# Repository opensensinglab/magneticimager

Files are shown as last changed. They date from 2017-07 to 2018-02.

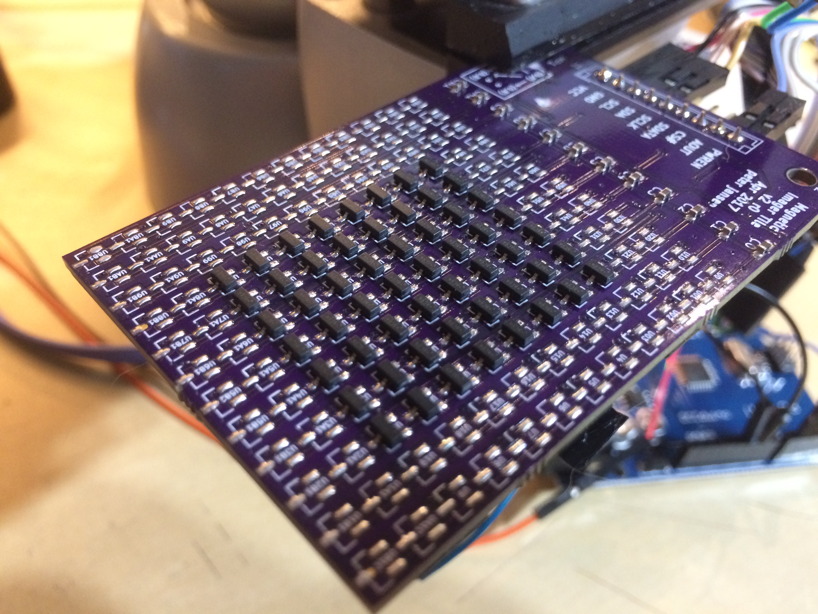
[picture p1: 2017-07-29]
hardware/version2r0/magnetic_tile_top.JPG

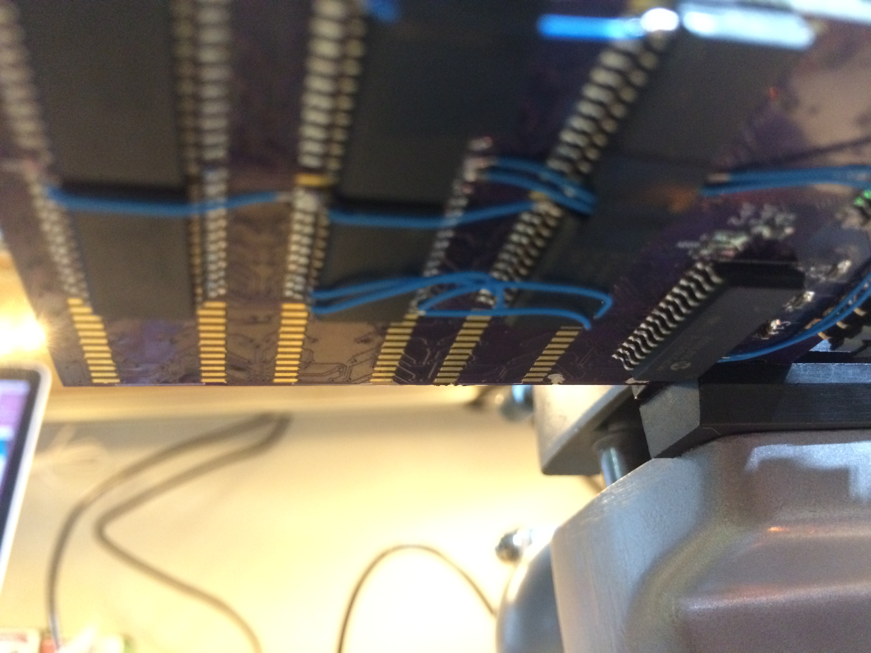
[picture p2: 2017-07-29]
hardware/version2r0/magnetic_tile_bottom.JPG

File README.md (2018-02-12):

Magnetic Imaging Tile
======

Work-in-progress.  Please use at your own risk. <br>

This is a board intended to function as a "magnetic field camera", and visualize magnetic fields. 

### Version 3.0

The major advancement of v3.0 is a dramatic increase in the speed with which the tile data can be read out.  I have achieved ~2000 frames per second (fps), which allows visualizing even quickly varying fields (e.g. those in a 60Hz transformer, or a moving motor), but it's likely that the tile can achieve even higher framerates.  Version 3.0 reduces the size of the tile to an 8x8 grid of hall effect sensors (64 total), arrayed in a 4mm grid.  The boards should also still be tile-able, with up to 4 of the boards tileable with minimal borders to create a 16x16 array. 

For more information (and a video of the v3.0 tile in use), please see: 
https://hackaday.io/project/18518-iteration-8/log/91551-a-third-high-speed-magnetic-imager-tile-draft

### Version 2.0

Version 2.0 consists of an array of 12x12 hall effect sensors (144 total) that sense magnetic fields, arrayed in a 4mm grid.  Each sensor is connected to an array of analog switches, that allow an individual sensor to be addressed.  Read out is accomplished one magnetic "pixel" at a time, selecting a given hall sensor from the array, reading it's value (either using the internal ADC, or an external ADC), and repeating this process until the entire array has been read out.  

The current array is designed to be tile-able, with up to four of the boards (24x24 magnetic field sensors) arrayed together. 

The Arduino firmware has a framerate of approximately 10 frames per second, when the image data is streamed over the serial port and displayed using the Processing visualization.  The Raspberry Pi Python example achieves approximately 30fps.  The array itself is likely capable of much higher speeds, but one of the major limiting factors is currently the speed of the I2C I/O multiplexer (used to select which magnetometer to read from). 

For more information (and a video of the v2.0 tile in use), please see: 
https://hackaday.io/project/18518-iteration-8/log/64376-a-magnetic-imager-tile

# Open Source

This project is open source software and hardware, and is released under various open licenses.

# Disclaimer

**DISCLAIMER OF WARRANTIES AND LIMITATION OF LIABILITY.**

UNLESS OTHERWISE SEPARATELY UNDERTAKEN BY THE LICENSOR, TO THE EXTENT POSSIBLE, THE LICENSOR OFFERS THE LICENSED MATERIAL AS-IS AND AS-AVAILABLE, AND MAKES NO REPRESENTATIONS OR WARRANTIES OF ANY KIND CONCERNING THE LICENSED MATERIAL, WHETHER EXPRESS, IMPLIED, STATUTORY, OR OTHER. THIS INCLUDES, WITHOUT LIMITATION, WARRANTIES OF TITLE, MERCHANTABILITY, FITNESS FOR A PARTICULAR PURPOSE, NON-INFRINGEMENT, ABSENCE OF LATENT OR OTHER DEFECTS, ACCURACY, OR THE PRESENCE OR ABSENCE OF ERRORS, WHETHER OR NOT KNOWN OR DISCOVERABLE. WHERE DISCLAIMERS OF WARRANTIES ARE NOT ALLOWED IN FULL OR IN PART, THIS DISCLAIMER MAY NOT APPLY TO YOU.

TO THE EXTENT POSSIBLE, IN NO EVENT WILL THE LICENSOR BE LIABLE TO YOU ON ANY LEGAL THEORY (INCLUDING, WITHOUT LIMITATION, NEGLIGENCE) OR OTHERWISE FOR ANY DIRECT, SPECIAL, INDIRECT, INCIDENTAL, CONSEQUENTIAL, PUNITIVE, EXEMPLARY, OR OTHER LOSSES, COSTS, EXPENSES, OR DAMAGES ARISING OUT OF THIS PUBLIC LICENSE OR USE OF THE LICENSED MATERIAL, EVEN IF THE LICENSOR HAS BEEN ADVISED OF THE POSSIBILITY OF SUCH LOSSES, COSTS, EXPENSES, OR DAMAGES. WHERE A LIMITATION OF LIABILITY IS NOT ALLOWED IN FULL OR IN PART, THIS LIMITATION MAY NOT APPLY TO YOU.

THE DISCLAIMER OF WARRANTIES AND LIMITATION OF LIABILITY PROVIDED ABOVE SHALL BE INTERPRETED IN A MANNER THAT, TO THE EXTENT POSSIBLE, MOST CLOSELY APPROXIMATES AN ABSOLUTE DISCLAIMER AND WAIVER OF ALL LIABILITY.

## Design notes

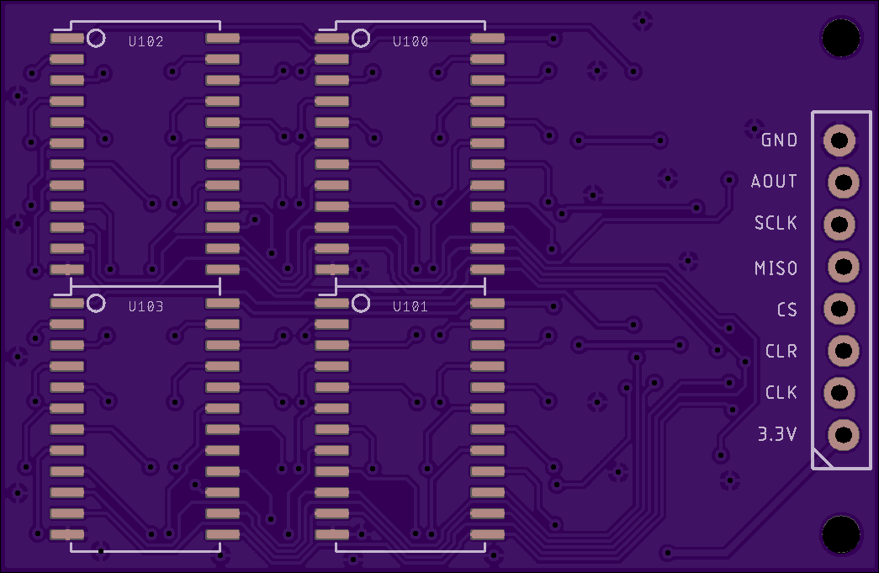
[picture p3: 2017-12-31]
hardware/version3r0/board_bottom.png

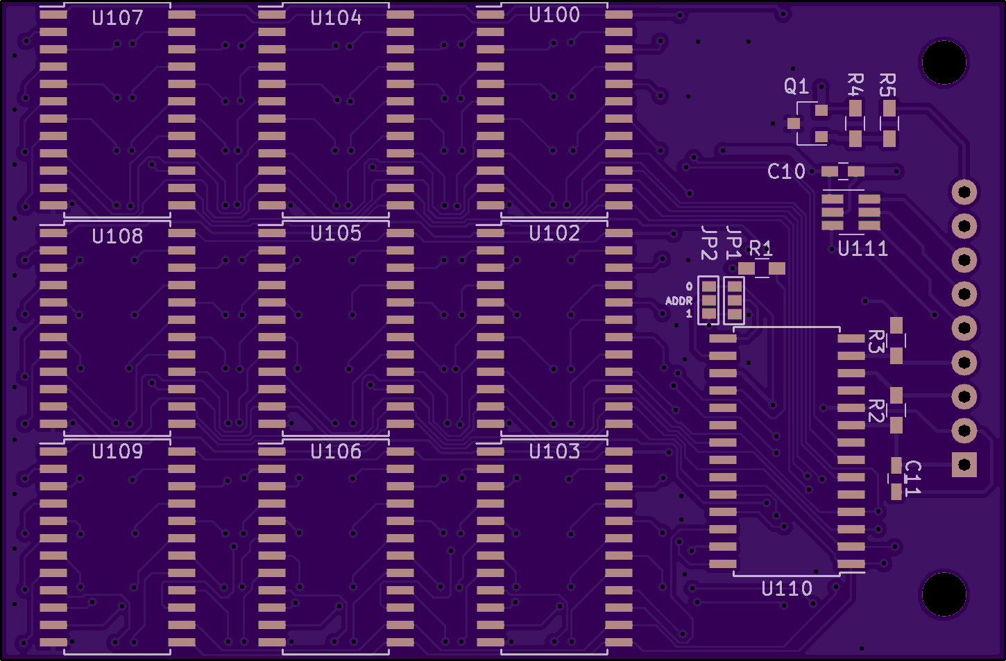
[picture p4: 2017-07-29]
hardware/version2r0/board_bottom.png

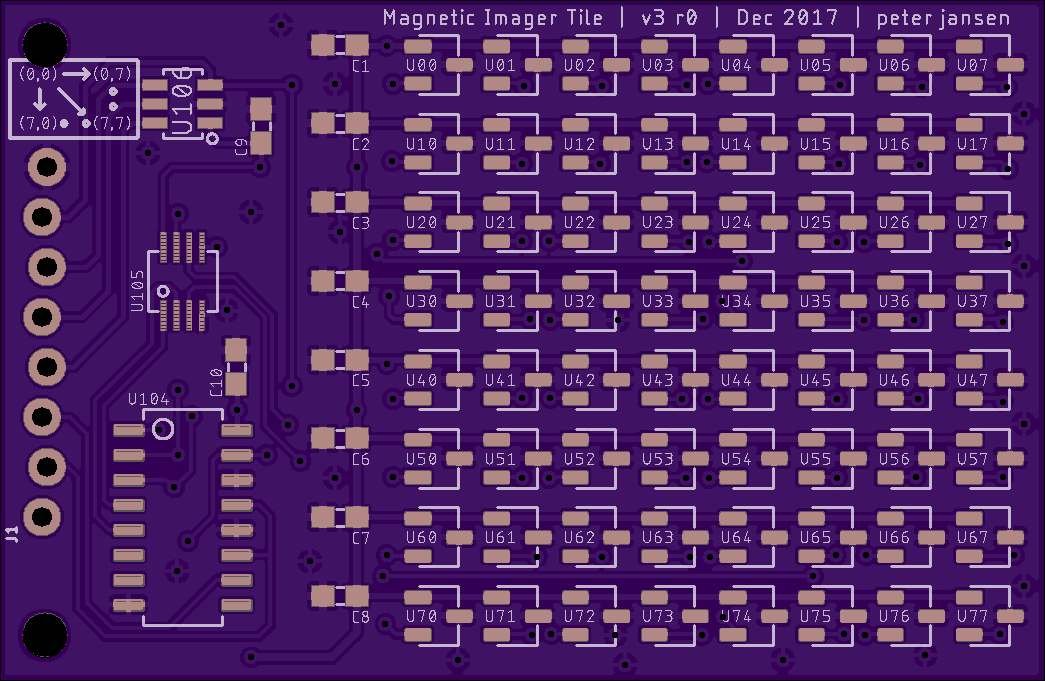
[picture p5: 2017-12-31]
hardware/version3r0/board_top.png

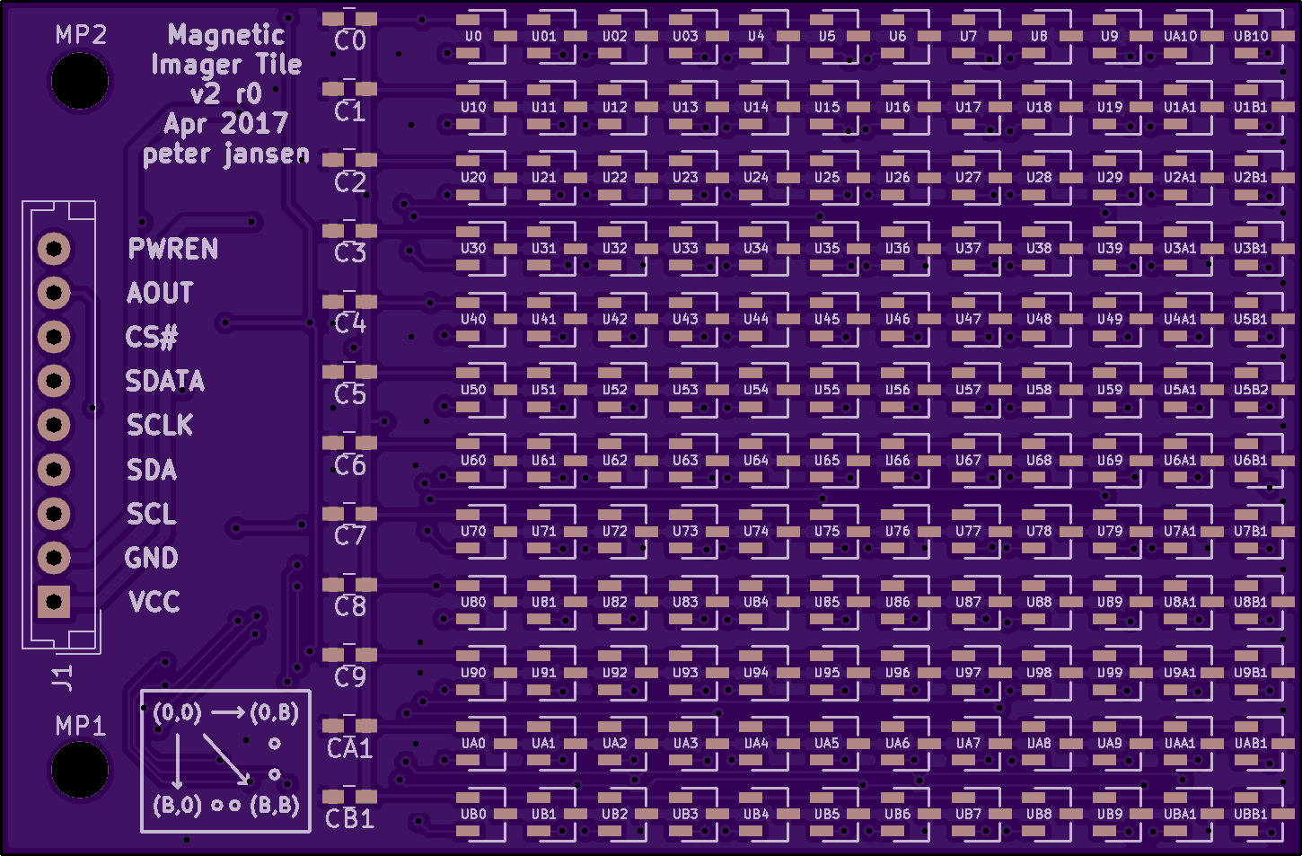
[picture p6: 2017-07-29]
hardware/version2r0/board_top.png

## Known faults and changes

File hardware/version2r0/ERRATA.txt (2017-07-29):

KNOWN ERRATA:
Version 2 revision 0
- The MOSFET to enable power (Q1) did not function, and is likely wired incorrectly.  The fix for this (if you've already made one of the boards without fixing the source) is to remove Q1, and add a small jumper so that the power is always enabled.

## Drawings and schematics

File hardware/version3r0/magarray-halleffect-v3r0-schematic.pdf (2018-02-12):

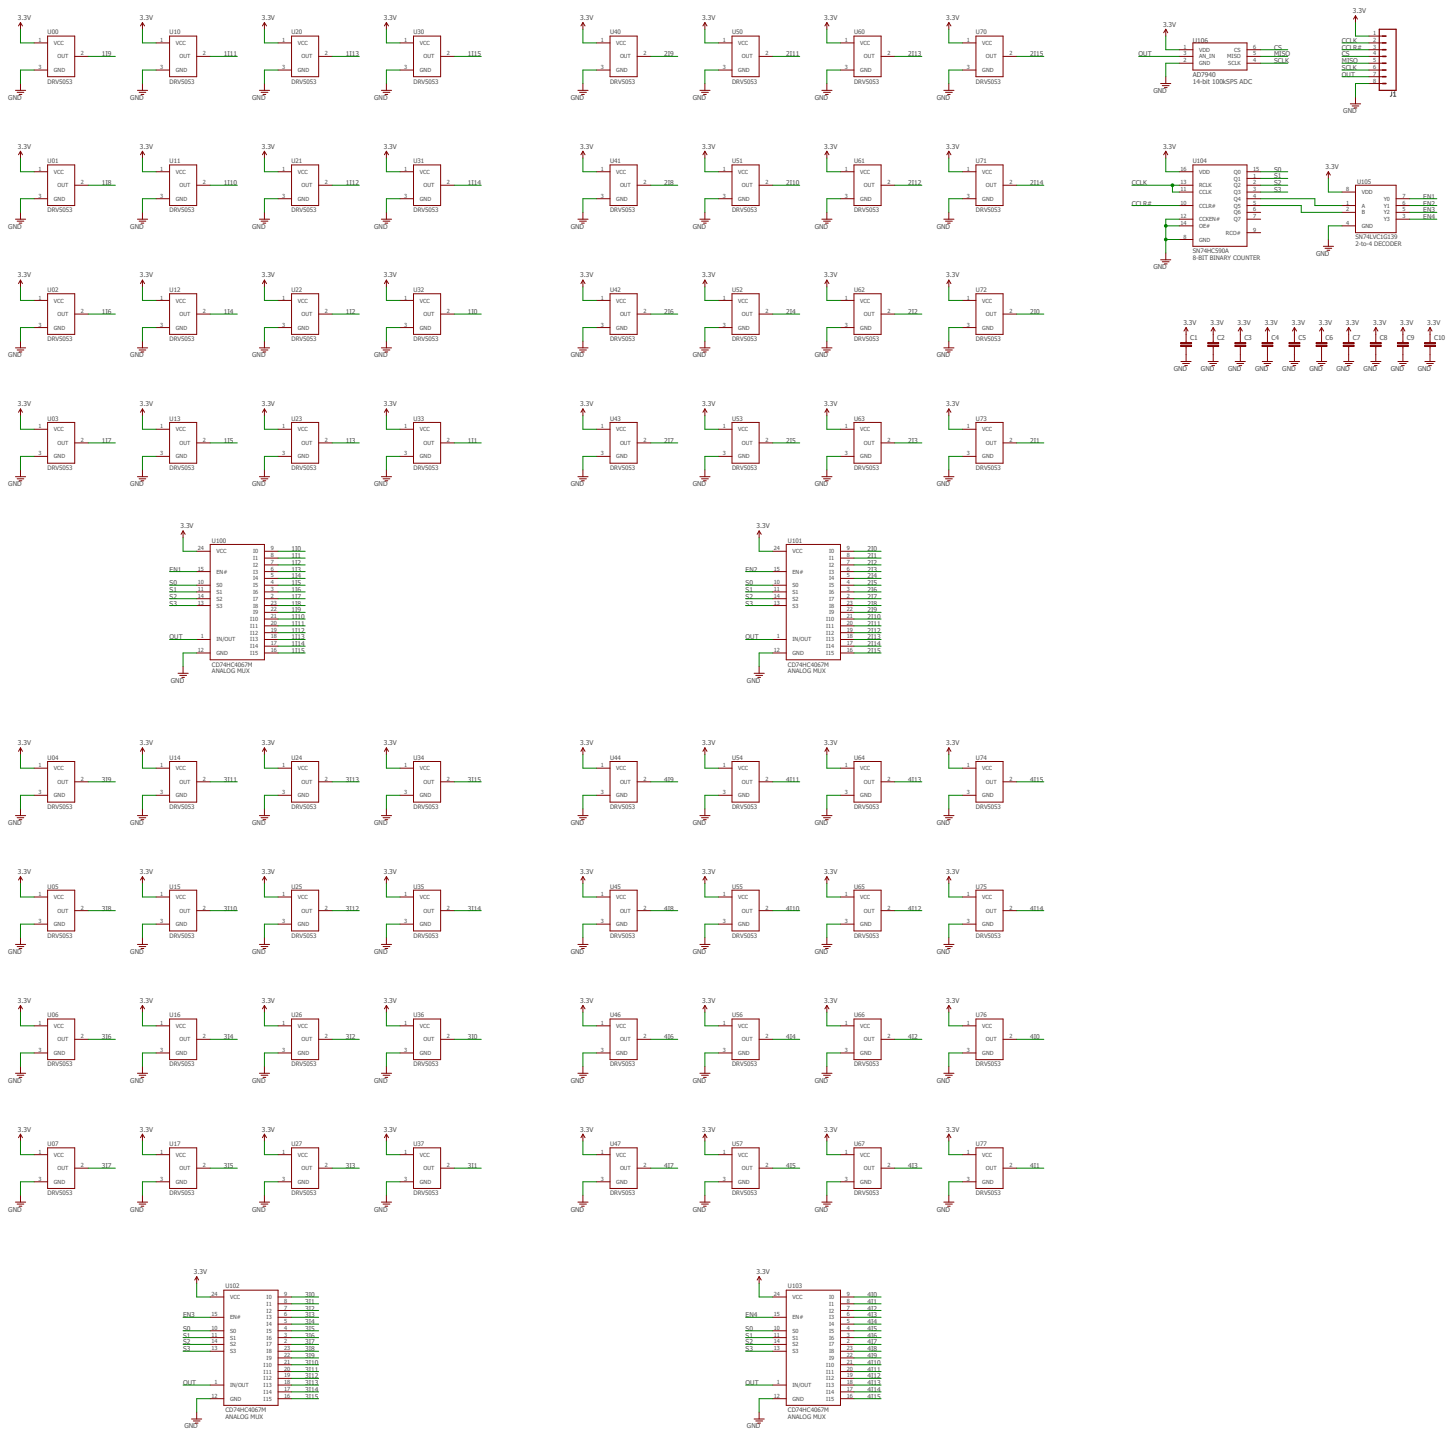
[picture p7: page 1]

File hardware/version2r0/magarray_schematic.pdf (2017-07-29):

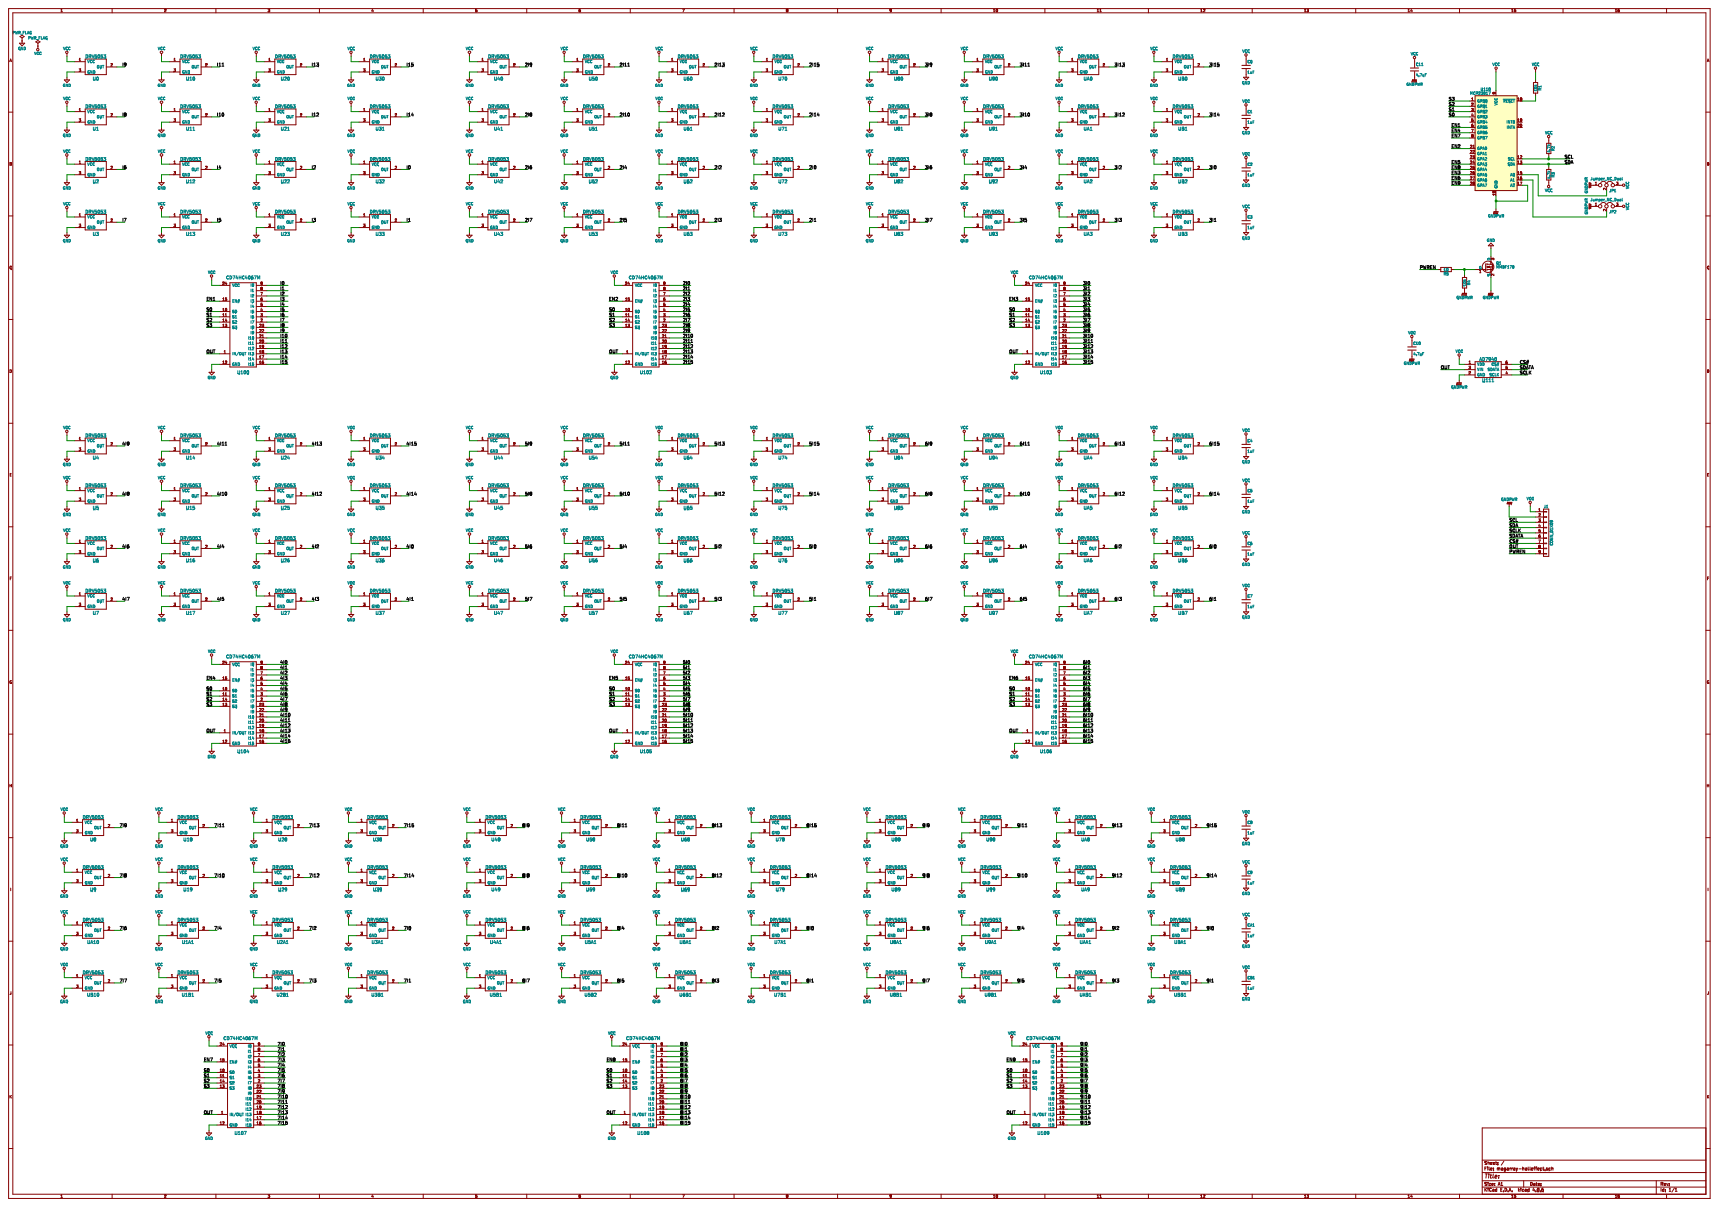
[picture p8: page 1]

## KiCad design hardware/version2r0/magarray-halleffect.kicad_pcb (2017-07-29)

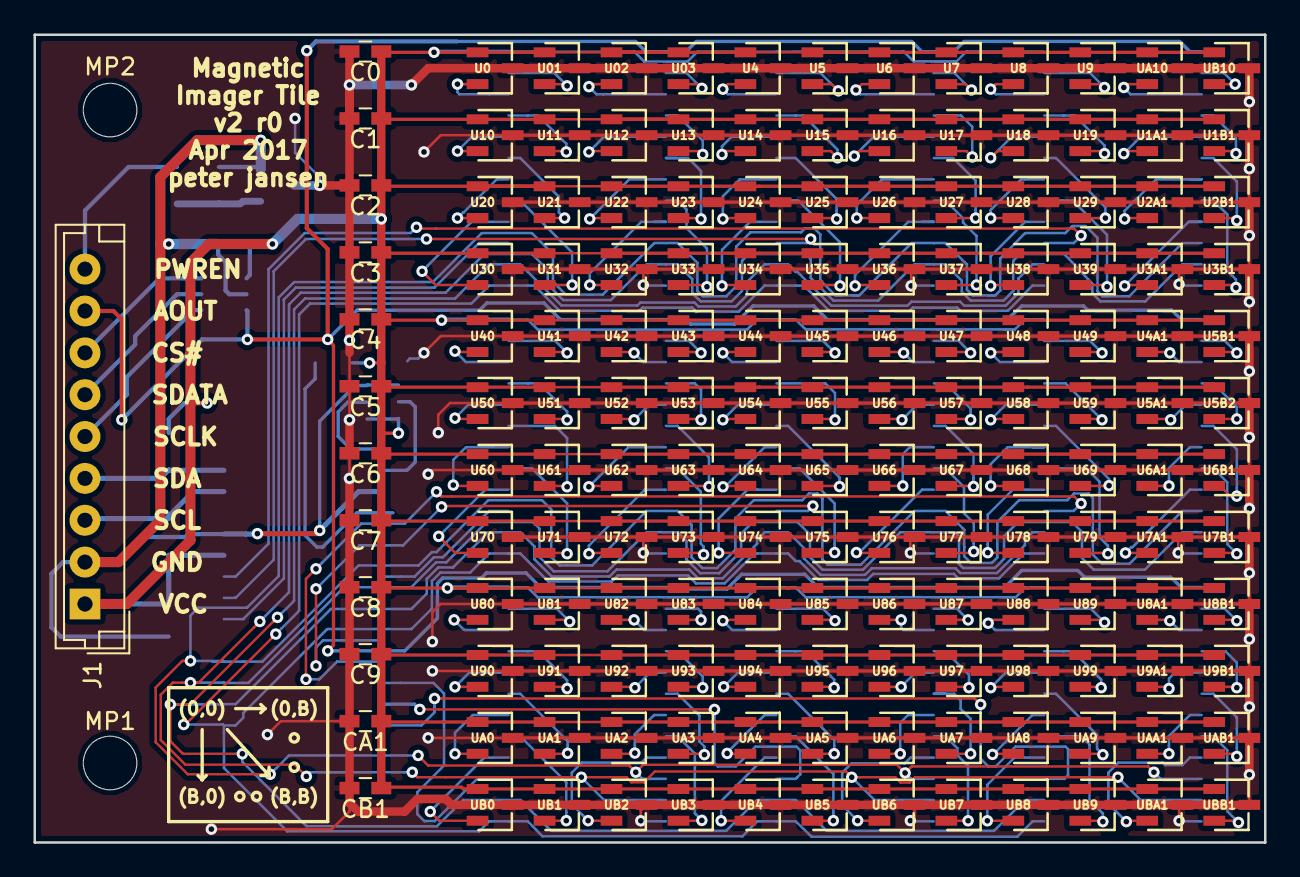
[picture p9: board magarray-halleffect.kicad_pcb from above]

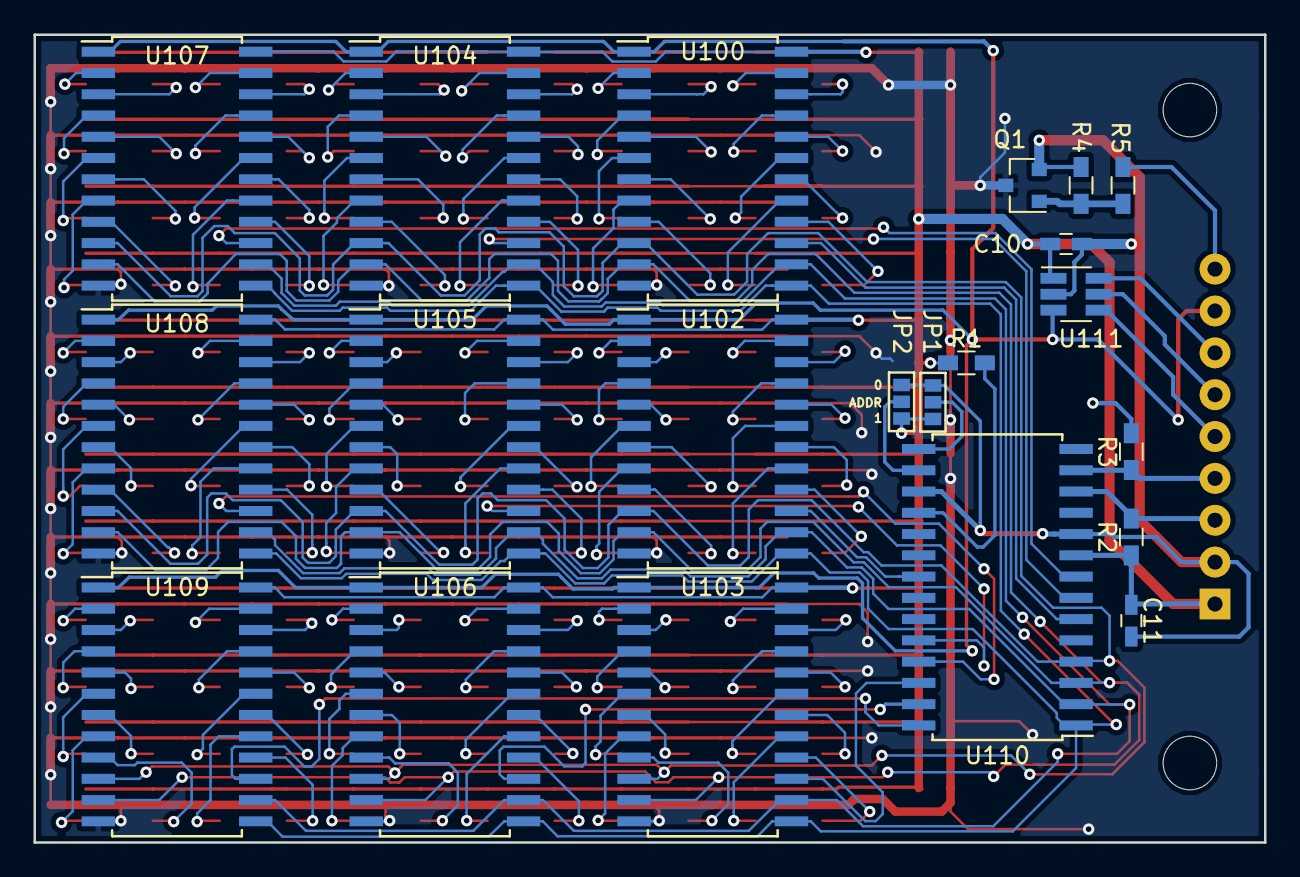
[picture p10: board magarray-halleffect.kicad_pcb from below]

Board: 2 copper layers, 73.5 x 48.2 mm, 180 parts (21 on the bottom side), 171 nets.

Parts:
C0, C1, C2, C3, C4, C5, C6, C7, C8, C9: 1uF; C_0603_HandSoldering
C10, C11: 4.7uF; C_0603_HandSoldering
CA1: 1uF; C_0603_HandSoldering
CB1: 1uF; C_0603_HandSoldering
J1: CONN_01X09; JST_EH_B09B-EH-A_09x2.50mm_Straight
JP1, JP2: Jumper_NC_Dual; SOLDERJUMPER-2WAY
MP1, MP2: MountingHole_3.2mm_M3
Q1: MMBF170; SOT-23
R1, R4: 10k; R_0603_HandSoldering
R2, R3: 4.7k; R_0603_HandSoldering
R5: 10; R_0603_HandSoldering
U0, U01, U1A1, U1B1, U02, U2A1, U2B1, U03, U3A1, U3B1, U4, U4A1, U5, U5A1, U5B1, U5B2, U6, U6A1, U6B1, U7, U7A1, U7B1, U8, U8A1, U8B1, U9, U9A1, U9B1, U10, U11, U12, U13, U14, U15, U16, U17, U18, U19, U20, U21, U22, U23, U24, U25, U26, U27, U28, U29, U30, U31, U32, U33, U34, U35, U36, U37, U38, U39, U40, U41, U42, U43, U44, U45, U46, U47, U48, U49, U50, U51, U52, U53, U54, U55, U56, U57, U58, U59, U60, U61, U62, U63, U64, U65, U66, U67, U68, U69, U70, U71, U72, U73, U74, U75, U76, U77, U78, U79, U80, U81, U82, U83, U84, U85, U86, U87, U88, U89, U90, U91, U92, U93, U94, U95, U96, U97, U98, U99: DRV5053; SOT-23
U100, U102, U103, U104, U105, U106, U107, U108, U109: CD74HC4067M; SOIC-24W_7.5x15.4mm_Pitch1.27mm
U110: MCP23017; SOIC-28W_7.5x17.9mm_Pitch1.27mm
U111: AD7940; SOT-23-6_Handsoldering
UA0, UA1, UA2, UA3, UA4, UA5, UA6, UA7, UA8, UA9, UA10: DRV5053; SOT-23
UAA1: DRV5053; SOT-23
UAB1: DRV5053; SOT-23
UB0, UB1, UB2, UB3, UB4, UB5, UB6, UB7, UB8, UB9, UB10: DRV5053; SOT-23
UBA1: DRV5053; SOT-23
UBB1: DRV5053; SOT-23

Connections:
/2I0: U72.2, U102.9
/2I1: U73.2, U102.8
/2I2: U62.2, U102.7
/2I3: U63.2, U102.6
/2I4: U52.2, U102.5
/2I5: U53.2, U102.4
/2I6: U42.2, U102.3
/2I7: U43.2, U102.2
/2I8: U41.2, U102.23
/2I9: U40.2, U102.22
/2I10: U51.2, U102.21
/2I11: U50.2, U102.20
/2I12: U61.2, U102.19
/2I13: U60.2, U102.18
/2I14: U71.2, U102.17
/2I15: U70.2, U102.16
/3I0: U103.9, UB2.2
/3I1: U103.8, UB3.2
/3I2: U103.7, UA2.2
/3I3: U103.6, UA3.2
/3I4: U92.2, U103.5
/3I5: U93.2, U103.4
/3I6: U82.2, U103.3
/3I7: U83.2, U103.2
/3I8: U81.2, U103.23
/3I9: U80.2, U103.22
/3I10: U91.2, U103.21
/3I11: U90.2, U103.20
/3I12: U103.19, UA1.2
/3I13: U103.18, UA0.2
/3I14: U103.17, UB1.2
/3I15: U103.16, UB0.2
/4I0: U36.2, U104.9
/4I1: U37.2, U104.8
/4I2: U26.2, U104.7
/4I3: U27.2, U104.6
/4I4: U16.2, U104.5
/4I5: U17.2, U104.4
/4I6: U6.2, U104.3
/4I7: U7.2, U104.2
/4I8: U5.2, U104.23
/4I9: U4.2, U104.22
/4I10: U15.2, U104.21
/4I11: U14.2, U104.20
/4I12: U25.2, U104.19
/4I13: U24.2, U104.18
/4I14: U35.2, U104.17
/4I15: U34.2, U104.16
/5I0: U76.2, U105.9
/5I1: U77.2, U105.8
/5I2: U66.2, U105.7
/5I3: U67.2, U105.6
/5I4: U56.2, U105.5
/5I5: U57.2, U105.4
/5I6: U46.2, U105.3
/5I7: U47.2, U105.2
/5I8: U45.2, U105.23
/5I9: U44.2, U105.22
/5I10: U55.2, U105.21
/5I11: U54.2, U105.20
/5I12: U65.2, U105.19
/5I13: U64.2, U105.18
/5I14: U75.2, U105.17
/5I15: U74.2, U105.16
/6I0: U106.9, UB6.2
/6I1: U106.8, UB7.2
/6I2: U106.7, UA6.2
/6I3: U106.6, UA7.2
/6I4: U96.2, U106.5
/6I5: U97.2, U106.4
/6I6: U86.2, U106.3
/6I7: U87.2, U106.2
/6I8: U85.2, U106.23
/6I9: U84.2, U106.22
/6I10: U95.2, U106.21
/6I11: U94.2, U106.20
/6I12: U106.19, UA5.2
/6I13: U106.18, UA4.2
/6I14: U106.17, UB5.2
/6I15: U106.16, UB4.2
/7I0: U3A1.2, U107.9
/7I1: U3B1.2, U107.8
/7I2: U2A1.2, U107.7
/7I3: U2B1.2, U107.6
/7I4: U1A1.2, U107.5
/7I5: U1B1.2, U107.4
/7I6: U107.3, UA10.2
/7I7: U107.2, UB10.2
/7I8: U9.2, U107.23
/7I9: U8.2, U107.22
/7I10: U19.2, U107.21
/7I11: U18.2, U107.20
/7I12: U29.2, U107.19
/7I13: U28.2, U107.18
/7I14: U39.2, U107.17
/7I15: U38.2, U107.16
/8I0: U7A1.2, U108.9
/8I1: U7B1.2, U108.8
/8I2: U6A1.2, U108.7
/8I3: U6B1.2, U108.6
/8I4: U5A1.2, U108.5
/8I5: U5B2.2, U108.4
/8I6: U4A1.2, U108.3
/8I7: U5B1.2, U108.2
/8I8: U49.2, U108.23
/8I9: U48.2, U108.22
/8I10: U59.2, U108.21
/8I11: U58.2, U108.20
/8I12: U69.2, U108.19
/8I13: U68.2, U108.18
/8I14: U79.2, U108.17
/8I15: U78.2, U108.16
/9I0: U109.9, UBA1.2
/9I1: U109.8, UBB1.2
/9I2: U109.7, UAA1.2
/9I3: U109.6, UAB1.2
/9I4: U9A1.2, U109.5
/9I5: U9B1.2, U109.4
/9I6: U8A1.2, U109.3
/9I7: U8B1.2, U109.2
/9I8: U89.2, U109.23
/9I9: U88.2, U109.22
/9I10: U99.2, U109.21
/9I11: U98.2, U109.20
/9I12: U109.19, UA9.2
/9I13: U109.18, UA8.2
/9I14: U109.17, UB9.2
/9I15: U109.16, UB8.2
/CS#: J1.7, U111.6
/EN1: U100.15, U110.6
/EN2: U102.15, U110.21
/EN3: U103.15, U110.26
/EN4: U104.15, U110.7
/EN5: U105.15, U110.24
/EN6: U106.15, U110.27
/EN7: U107.15, U110.8
/EN8: U108.15, U110.25
/EN9: U109.15, U110.28
/I0: U32.2, U100.9
/I1: U33.2, U100.8
/I2: U22.2, U100.7
/I3: U23.2, U100.6
/I4: U12.2, U100.5
/I5: U13.2, U100.4
/I6: U02.2, U100.3
/I7: U03.2, U100.2
/I8: U01.2, U100.23
/I9: U0.2, U100.22
/I10: U11.2, U100.21
/I11: U10.2, U100.20
/I12: U21.2, U100.19
/I13: U20.2, U100.18
/I14: U31.2, U100.17
/I15: U30.2, U100.16
/OUT: J1.8, U100.1, U102.1, U103.1, U104.1, U105.1, U106.1, U107.1, U108.1, U109.1, U111.3
/PWREN: J1.9, R5.2
/S0: U100.10, U102.10, U103.10, U104.10, U105.10, U106.10, U107.10, U108.10, U109.10, U110.4
/S1: U100.11, U102.11, U103.11, U104.11, U105.11, U106.11, U107.11, U108.11, U109.11, U110.3
/S2: U100.14, U102.14, U103.14, U104.14, U105.14, U106.14, U107.14, U108.14, U109.14, U110.2
/S3: U100.13, U102.13, U103.13, U104.13, U105.13, U106.13, U107.13, U108.13, U109.13, U110.1
/SCL: J1.3, R2.2, U110.12
/SCLK: J1.5, U111.4
/SDA: J1.4, R3.1, U110.13
/SDATA: J1.6, U111.5
GND: C0.2, C1.2, C2.2, C3.2, C4.2, C5.2, C6.2, C7.2, C8.2, C9.2, CA1.2, CB1.2, Q1.3, U0.3, U01.3, U1A1.3, U1B1.3, U02.3, U2A1.3, U2B1.3, U03.3, U3A1.3, U3B1.3, U4.3, U4A1.3, U5.3, U5A1.3, U5B1.3, U5B2.3, U6.3, U6A1.3, U6B1.3, U7.3, U7A1.3, U7B1.3, U8.3, U8A1.3, U8B1.3, U9.3, U9A1.3, U9B1.3, U10.3, U11.3, U12.3, U13.3, U14.3, U15.3, U16.3, U17.3, U18.3, U19.3, U20.3, U21.3, U22.3, U23.3, U24.3, U25.3, U26.3, U27.3, U28.3, U29.3, U30.3, U31.3, U32.3, U33.3, U34.3, U35.3, U36.3, U37.3, U38.3, U39.3, U40.3, U41.3, U42.3, U43.3, U44.3, U45.3, U46.3, U47.3, U48.3, U49.3, U50.3, U51.3, U52.3, U53.3, U54.3, U55.3, U56.3, U57.3, U58.3, U59.3, U60.3, U61.3, U62.3, U63.3, U64.3, U65.3, U66.3, U67.3, U68.3, U69.3, U70.3, U71.3, U72.3, U73.3, U74.3, U75.3, U76.3, U77.3, U78.3, U79.3, U80.3, U81.3, U82.3, U83.3, U84.3, U85.3, U86.3, U87.3, U88.3, U89.3, U90.3, U91.3, U92.3, U93.3, U94.3, U95.3, U96.3, U97.3, U98.3, U99.3, U100.12, U102.12, U103.12, U104.12, U105.12, U106.12, U107.12, U108.12, U109.12, UA0.3, UA1.3, UA2.3, UA3.3, UA4.3, UA5.3, UA6.3, UA7.3, UA8.3, UA9.3, UA10.3, UAA1.3, UAB1.3, UB0.3, UB1.3, UB2.3, UB3.3, UB4.3, UB5.3, UB6.3, UB7.3, UB8.3, UB9.3, UB10.3, UBA1.3, UBB1.3
GNDPWR: C10.2, C11.2, J1.2, JP1.1, JP2.1, Q1.2, R4.2, U110.10, U110.17, U111.2
unnamed: JP1.2, U110.15
unnamed: JP2.2, U110.16
unnamed: Q1.1, R4.1, R5.1
unnamed: R1.2, U110.18
VCC: C0.1, C1.1, C2.1, C3.1, C4.1, C5.1, C6.1, C7.1, C8.1, C9.1, C10.1, C11.1, CA1.1, CB1.1, J1.1, JP1.3, JP2.3, R1.1, R2.1, R3.2, U0.1, U01.1, U1A1.1, U1B1.1, U02.1, U2A1.1, U2B1.1, U03.1, U3A1.1, U3B1.1, U4.1, U4A1.1, U5.1, U5A1.1, U5B1.1, U5B2.1, U6.1, U6A1.1, U6B1.1, U7.1, U7A1.1, U7B1.1, U8.1, U8A1.1, U8B1.1, U9.1, U9A1.1, U9B1.1, U10.1, U11.1, U12.1, U13.1, U14.1, U15.1, U16.1, U17.1, U18.1, U19.1, U20.1, U21.1, U22.1, U23.1, U24.1, U25.1, U26.1, U27.1, U28.1, U29.1, U30.1, U31.1, U32.1, U33.1, U34.1, U35.1, U36.1, U37.1, U38.1, U39.1, U40.1, U41.1, U42.1, U43.1, U44.1, U45.1, U46.1, U47.1, U48.1, U49.1, U50.1, U51.1, U52.1, U53.1, U54.1, U55.1, U56.1, U57.1, U58.1, U59.1, U60.1, U61.1, U62.1, U63.1, U64.1, U65.1, U66.1, U67.1, U68.1, U69.1, U70.1, U71.1, U72.1, U73.1, U74.1, U75.1, U76.1, U77.1, U78.1, U79.1, U80.1, U81.1, U82.1, U83.1, U84.1, U85.1, U86.1, U87.1, U88.1, U89.1, U90.1, U91.1, U92.1, U93.1, U94.1, U95.1, U96.1, U97.1, U98.1, U99.1, U100.24, U102.24, U103.24, U104.24, U105.24, U106.24, U107.24, U108.24, U109.24, U110.9, U111.1, UA0.1, UA1.1, UA2.1, UA3.1, UA4.1, UA5.1, UA6.1, UA7.1, UA8.1, UA9.1, UA10.1, UAA1.1, UAB1.1, UB0.1, UB1.1, UB2.1, UB3.1, UB4.1, UB5.1, UB6.1, UB7.1, UB8.1, UB9.1, UB10.1, UBA1.1, UBB1.1

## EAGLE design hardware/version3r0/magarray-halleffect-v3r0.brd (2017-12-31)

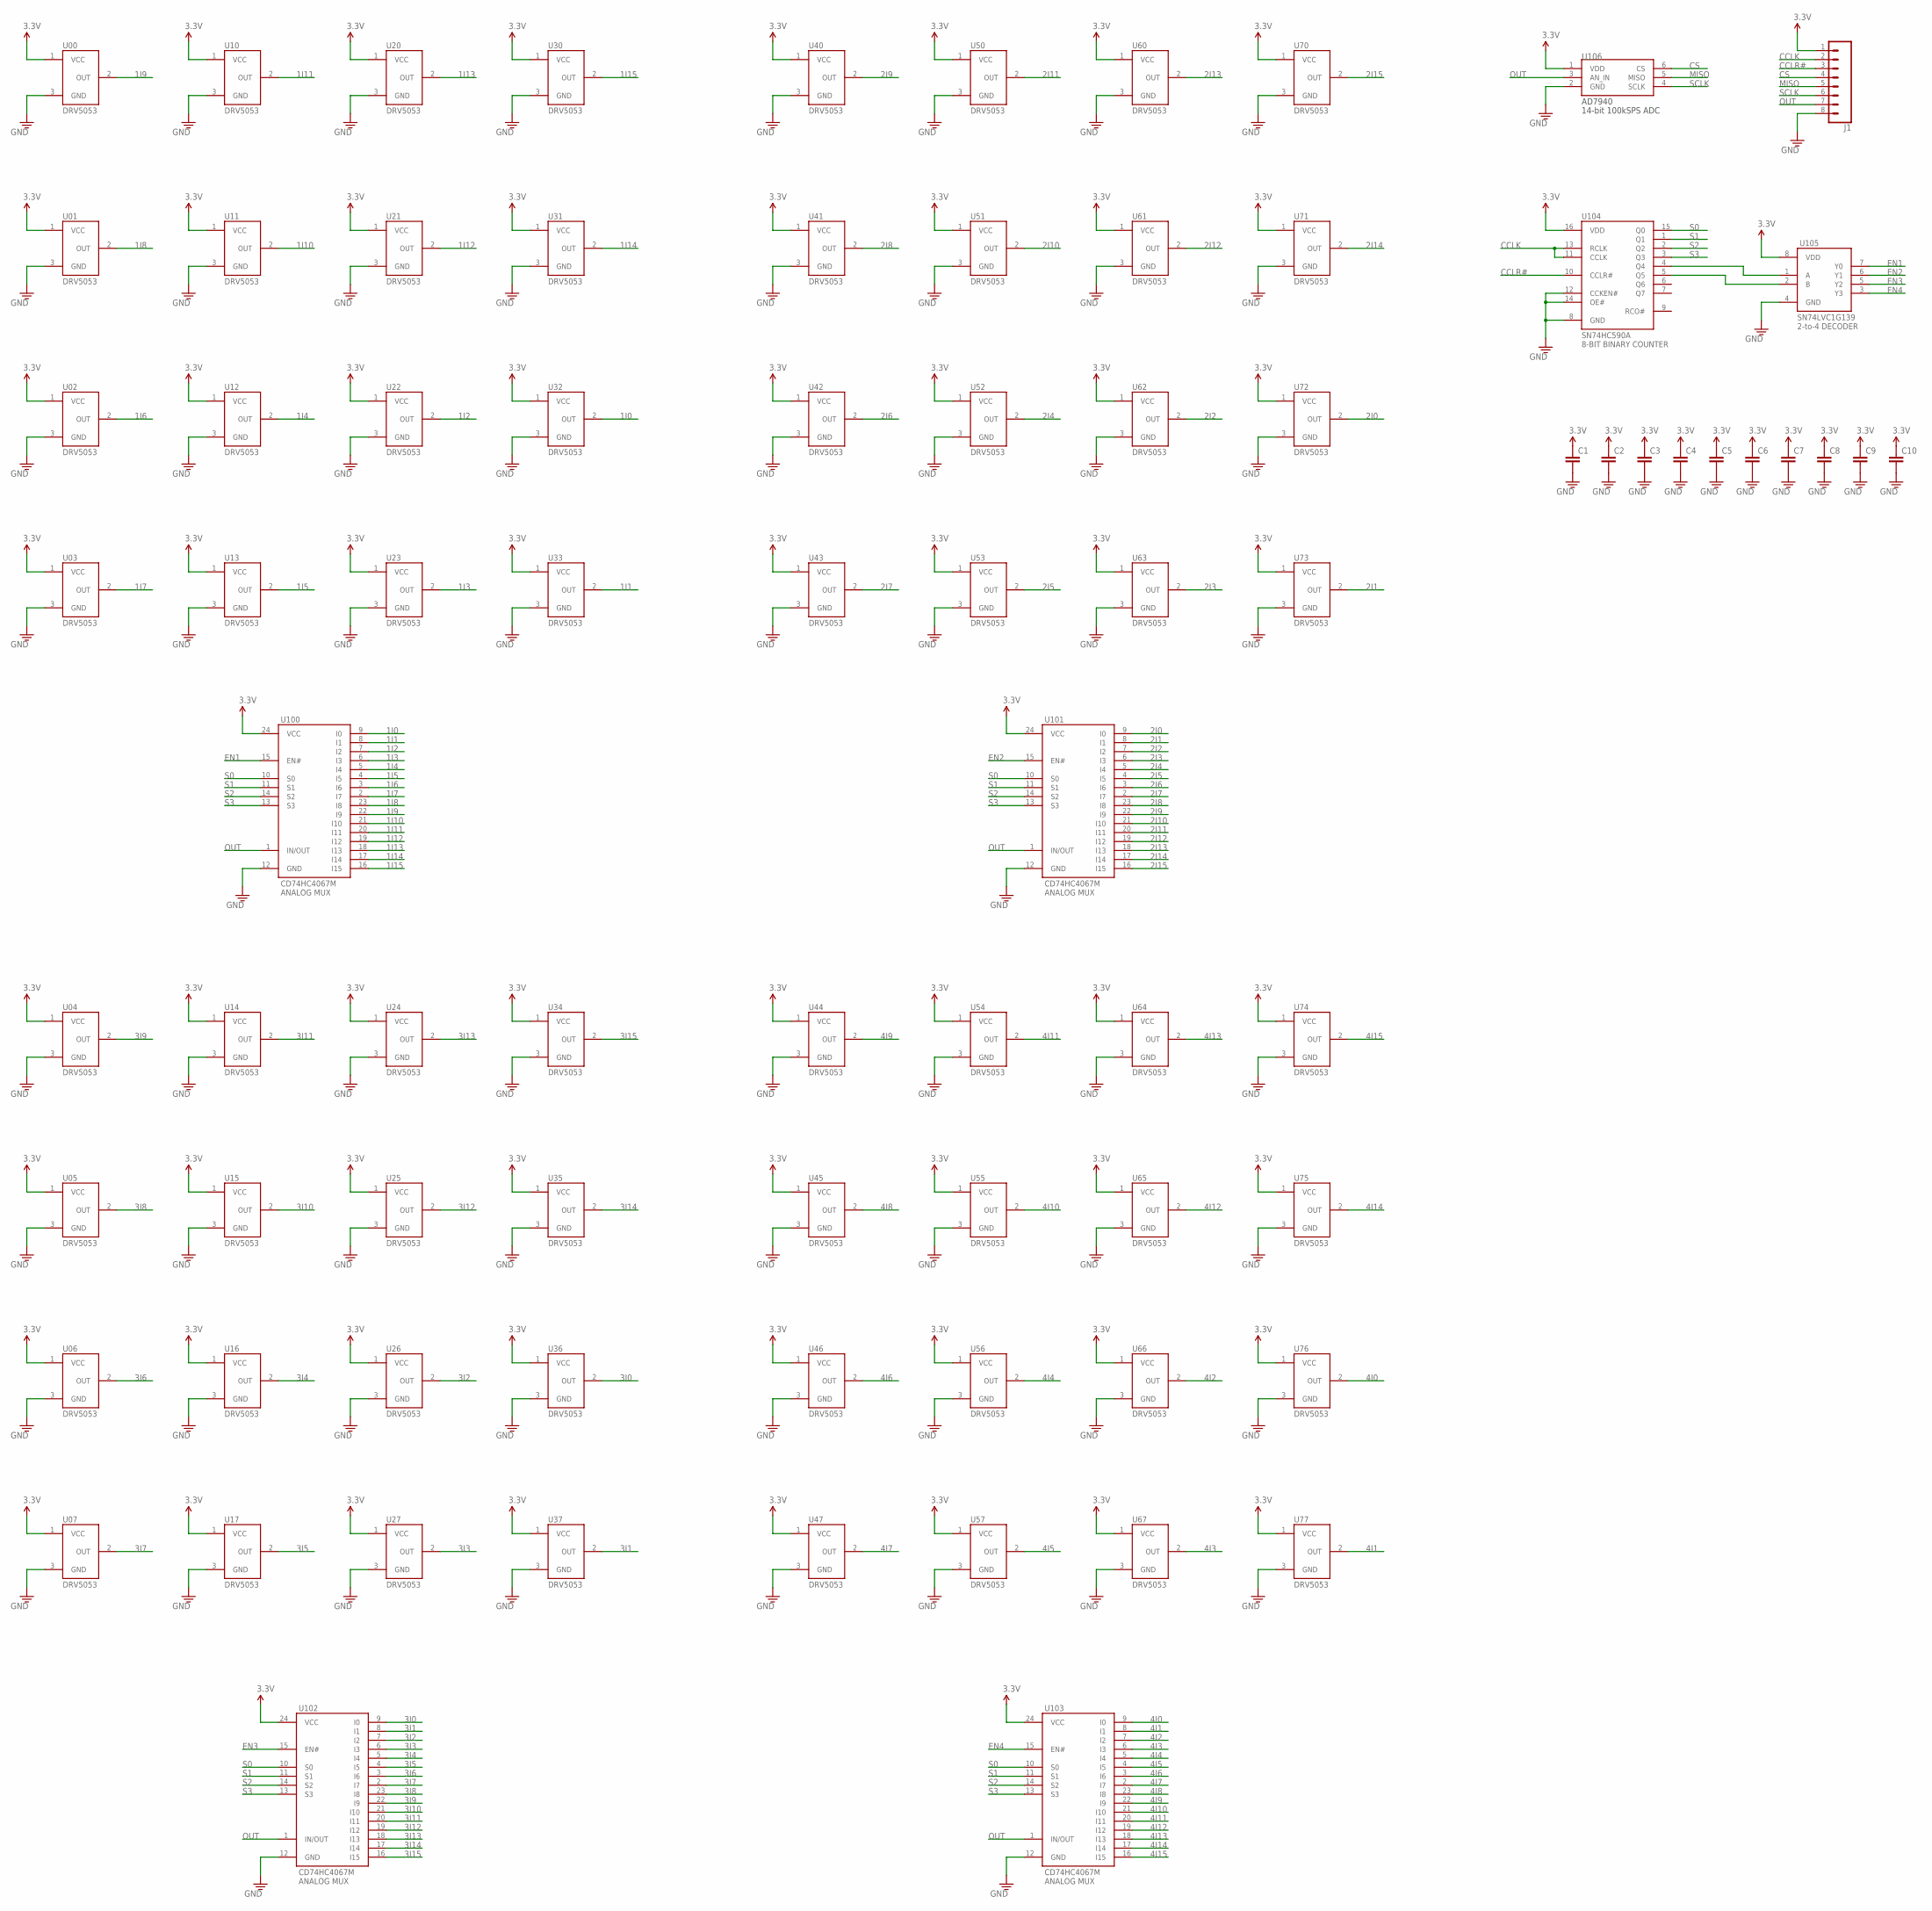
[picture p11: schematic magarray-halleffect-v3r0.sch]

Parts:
C1, C2, C3, C4, C5, C6, C7, C8, C9, C10: CAP0603; 0603
J1: CONN_08LOCK_NO_SILK; 1X08_LOCK_NO_SILK
U00, U01, U02, U03, U04, U05, U06, U07, U10, U11, U12, U13, U14, U15, U16, U17, U20, U21, U22, U23, U24, U25, U26, U27, U30, U31, U32, U33, U34, U35, U36, U37, U40, U41, U42, U43, U44, U45, U46, U47, U50, U51, U52, U53, U54, U55, U56, U57, U60, U61, U62, U63, U64, U65, U66, U67, U70, U71, U72, U73, U74, U75, U76, U77: DRV5053; SOT-23
U100, U101, U102, U103: CD74HC4067M; SOIC-24
U104: SN74HC509A; SO16
U105: SN74LVC1G139; SM8
U106: AD7940; SOT-23-6L

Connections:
1I0: U32.2 (OUT), U100.9 (I0)
1I1: U33.2 (OUT), U100.8 (I1)
1I2: U22.2 (OUT), U100.7 (I2)
1I3: U23.2 (OUT), U100.6 (I3)
1I4: U12.2 (OUT), U100.5 (I4)
1I5: U13.2 (OUT), U100.4 (I5)
1I6: U02.2 (OUT), U100.3 (I6)
1I7: U03.2 (OUT), U100.2 (I7)
1I8: U01.2 (OUT), U100.23 (I8)
1I9: U00.2 (OUT), U100.22 (I9)
1I10: U11.2 (OUT), U100.21 (I10)
1I11: U10.2 (OUT), U100.20 (I11)
1I12: U21.2 (OUT), U100.19 (I12)
1I13: U20.2 (OUT), U100.18 (I13)
1I14: U31.2 (OUT), U100.17 (I14)
1I15: U30.2 (OUT), U100.16 (I15)
2I0: U72.2 (OUT), U101.9 (I0)
2I1: U73.2 (OUT), U101.8 (I1)
2I2: U62.2 (OUT), U101.7 (I2)
2I3: U63.2 (OUT), U101.6 (I3)
2I4: U52.2 (OUT), U101.5 (I4)
2I5: U53.2 (OUT), U101.4 (I5)
2I6: U42.2 (OUT), U101.3 (I6)
2I7: U43.2 (OUT), U101.2 (I7)
2I8: U41.2 (OUT), U101.23 (I8)
2I9: U40.2 (OUT), U101.22 (I9)
2I10: U51.2 (OUT), U101.21 (I10)
2I11: U50.2 (OUT), U101.20 (I11)
2I12: U61.2 (OUT), U101.19 (I12)
2I13: U60.2 (OUT), U101.18 (I13)
2I14: U71.2 (OUT), U101.17 (I14)
2I15: U70.2 (OUT), U101.16 (I15)
3.3V: C1.1, C2.1, C3.1, C4.1, C5.1, C6.1, C7.1, C8.1, C9.1, C10.1, J1.1, U00.1 (VCC), U01.1 (VCC), U02.1 (VCC), U03.1 (VCC), U04.1 (VCC), U05.1 (VCC), U06.1 (VCC), U07.1 (VCC), U10.1 (VCC), U11.1 (VCC), U12.1 (VCC), U13.1 (VCC), U14.1 (VCC), U15.1 (VCC), U16.1 (VCC), U17.1 (VCC), U20.1 (VCC), U21.1 (VCC), U22.1 (VCC), U23.1 (VCC), U24.1 (VCC), U25.1 (VCC), U26.1 (VCC), U27.1 (VCC), U30.1 (VCC), U31.1 (VCC), U32.1 (VCC), U33.1 (VCC), U34.1 (VCC), U35.1 (VCC), U36.1 (VCC), U37.1 (VCC), U40.1 (VCC), U41.1 (VCC), U42.1 (VCC), U43.1 (VCC), U44.1 (VCC), U45.1 (VCC), U46.1 (VCC), U47.1 (VCC), U50.1 (VCC), U51.1 (VCC), U52.1 (VCC), U53.1 (VCC), U54.1 (VCC), U55.1 (VCC), U56.1 (VCC), U57.1 (VCC), U60.1 (VCC), U61.1 (VCC), U62.1 (VCC), U63.1 (VCC), U64.1 (VCC), U65.1 (VCC), U66.1 (VCC), U67.1 (VCC), U70.1 (VCC), U71.1 (VCC), U72.1 (VCC), U73.1 (VCC), U74.1 (VCC), U75.1 (VCC), U76.1 (VCC), U77.1 (VCC), U100.24 (VCC), U101.24 (VCC), U102.24 (VCC), U103.24 (VCC), U104.16 (VDD), U105.8 (VDD), U106.1 (VDD)
3I0: U36.2 (OUT), U102.9 (I0)
3I1: U37.2 (OUT), U102.8 (I1)
3I2: U26.2 (OUT), U102.7 (I2)
3I3: U27.2 (OUT), U102.6 (I3)
3I4: U16.2 (OUT), U102.5 (I4)
3I5: U17.2 (OUT), U102.4 (I5)
3I6: U06.2 (OUT), U102.3 (I6)
3I7: U07.2 (OUT), U102.2 (I7)
3I8: U05.2 (OUT), U102.23 (I8)
3I9: U04.2 (OUT), U102.22 (I9)
3I10: U15.2 (OUT), U102.21 (I10)
3I11: U14.2 (OUT), U102.20 (I11)
3I12: U25.2 (OUT), U102.19 (I12)
3I13: U24.2 (OUT), U102.18 (I13)
3I14: U35.2 (OUT), U102.17 (I14)
3I15: U34.2 (OUT), U102.16 (I15)
4I0: U76.2 (OUT), U103.9 (I0)
4I1: U77.2 (OUT), U103.8 (I1)
4I2: U66.2 (OUT), U103.7 (I2)
4I3: U67.2 (OUT), U103.6 (I3)
4I4: U56.2 (OUT), U103.5 (I4)
4I5: U57.2 (OUT), U103.4 (I5)
4I6: U46.2 (OUT), U103.3 (I6)
4I7: U47.2 (OUT), U103.2 (I7)
4I8: U45.2 (OUT), U103.23 (I8)
4I9: U44.2 (OUT), U103.22 (I9)
4I10: U55.2 (OUT), U103.21 (I10)
4I11: U54.2 (OUT), U103.20 (I11)
4I12: U65.2 (OUT), U103.19 (I12)
4I13: U64.2 (OUT), U103.18 (I13)
4I14: U75.2 (OUT), U103.17 (I14)
4I15: U74.2 (OUT), U103.16 (I15)
CCLK: J1.2, U104.11 (CCLK), U104.13 (RCLK)
CCLR#: J1.3, U104.10 (CCLR#)
CS: J1.4, U106.6 (CS)
EN1: U100.15 (EN#), U105.7 (Y0)
EN2: U101.15 (EN#), U105.6 (Y1)
EN3: U102.15 (EN#), U105.5 (Y2)
EN4: U103.15 (EN#), U105.3 (Y3)
GND: C1.2, C2.2, C3.2, C4.2, C5.2, C6.2, C7.2, C8.2, C9.2, C10.2, J1.8, U00.3 (GND), U01.3 (GND), U02.3 (GND), U03.3 (GND), U04.3 (GND), U05.3 (GND), U06.3 (GND), U07.3 (GND), U10.3 (GND), U11.3 (GND), U12.3 (GND), U13.3 (GND), U14.3 (GND), U15.3 (GND), U16.3 (GND), U17.3 (GND), U20.3 (GND), U21.3 (GND), U22.3 (GND), U23.3 (GND), U24.3 (GND), U25.3 (GND), U26.3 (GND), U27.3 (GND), U30.3 (GND), U31.3 (GND), U32.3 (GND), U33.3 (GND), U34.3 (GND), U35.3 (GND), U36.3 (GND), U37.3 (GND), U40.3 (GND), U41.3 (GND), U42.3 (GND), U43.3 (GND), U44.3 (GND), U45.3 (GND), U46.3 (GND), U47.3 (GND), U50.3 (GND), U51.3 (GND), U52.3 (GND), U53.3 (GND), U54.3 (GND), U55.3 (GND), U56.3 (GND), U57.3 (GND), U60.3 (GND), U61.3 (GND), U62.3 (GND), U63.3 (GND), U64.3 (GND), U65.3 (GND), U66.3 (GND), U67.3 (GND), U70.3 (GND), U71.3 (GND), U72.3 (GND), U73.3 (GND), U74.3 (GND), U75.3 (GND), U76.3 (GND), U77.3 (GND), U100.12 (GND), U101.12 (GND), U102.12 (GND), U103.12 (GND), U104.8 (GND), U104.12 (CCKEN#), U104.14 (OE#), U105.4 (GND), U106.2 (GND)
MISO: J1.5, U106.5 (MISO)
unnamed: U104.4 (Q4), U105.1 (A)
unnamed: U104.5 (Q5), U105.2 (B)
OUT: J1.7, U100.1 (IN/OUT), U101.1 (IN/OUT), U102.1 (IN/OUT), U103.1 (IN/OUT), U106.3 (AN_IN)
S0: U100.10 (S0), U101.10 (S0), U102.10 (S0), U103.10 (S0), U104.15 (Q0)
S1: U100.11 (S1), U101.11 (S1), U102.11 (S1), U103.11 (S1), U104.1 (Q1)
S2: U100.14 (S2), U101.14 (S2), U102.14 (S2), U103.14 (S2), U104.2 (Q2)
S3: U100.13 (S3), U101.13 (S3), U102.13 (S3), U103.13 (S3), U104.3 (Q3)
SCLK: J1.6, U106.4 (SCLK)

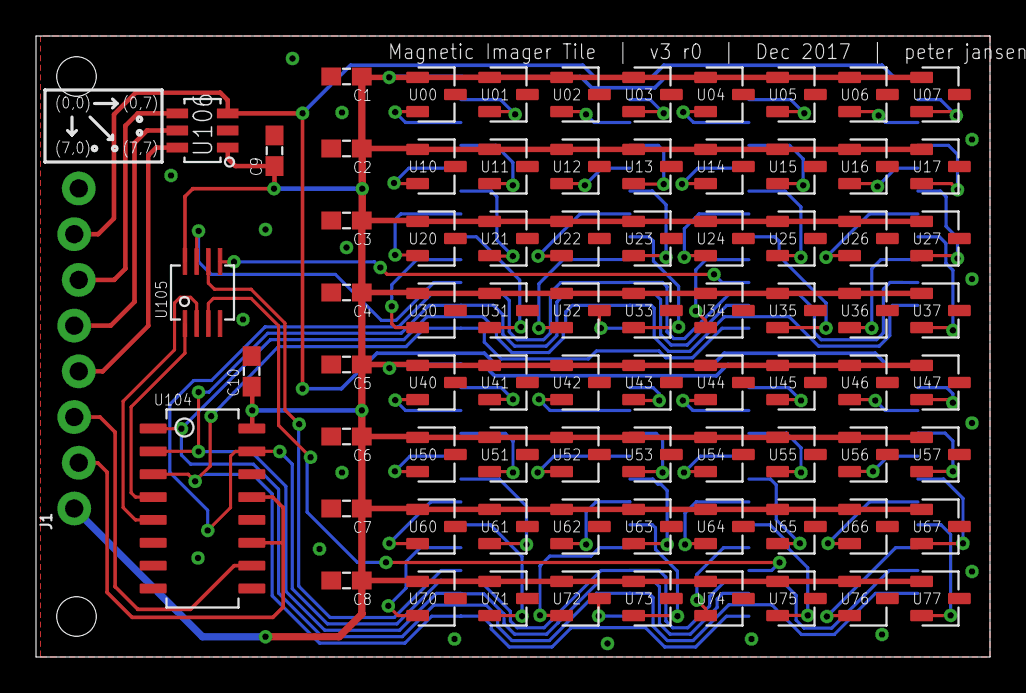
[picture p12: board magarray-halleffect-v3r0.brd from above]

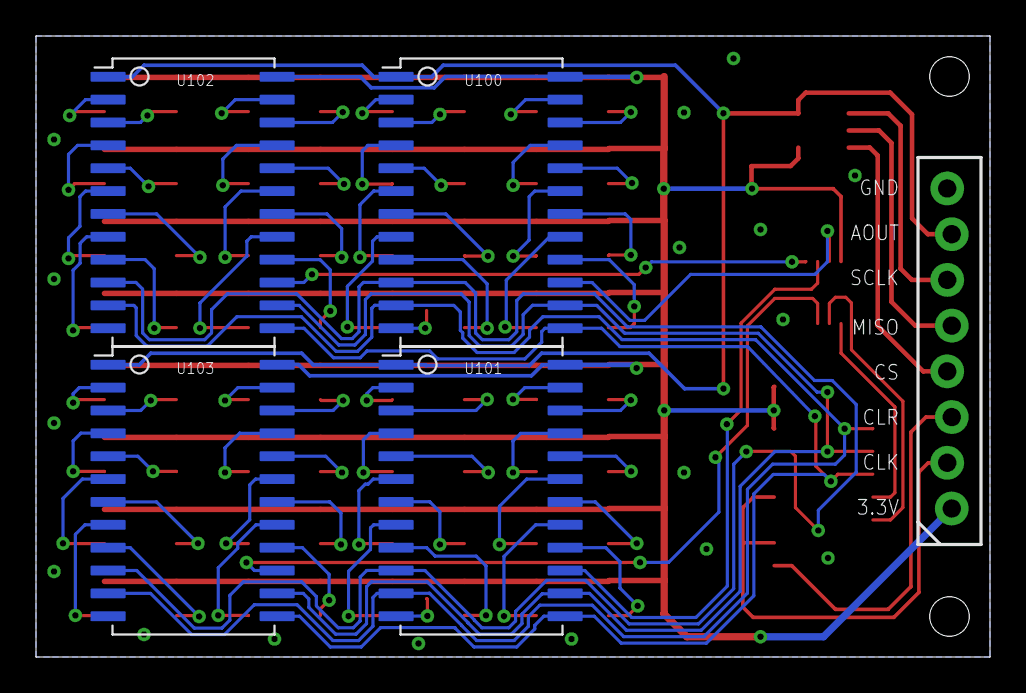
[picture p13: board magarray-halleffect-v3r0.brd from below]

Board: 2 copper layers, 53.0 x 34.5 mm, 82 parts (4 on the bottom side), 82 nets.

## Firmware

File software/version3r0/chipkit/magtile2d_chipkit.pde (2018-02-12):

// This basic example shows how to interface with the Magnetic Imaging Tile V3
// with a Chipkit MAX32, with data displayed via the serial port. 
// Simple serial commands allow viewing the data in a serial console, or
// sending the data to a program on a host system (such as the accompanying
// Processing example) for display. 
//
// The code primarily uses the internal ADC of the Chipkit MAX32, but
// (slow) code is also provided for using the AD7940 on the tile as 
// well.  The speed of the ADC and I/O clocking is essentially the
// limiting factor in framerate, and this should be kept in mind
// when porting to other platforms (e.g. the Arduino Uno). 
//
// The Chipkit MAX32 provides ~128K of RAM, which is enough for a
// short framebuffer (up to about 500 frames) when recording
// high-speed data. 
//
// This code was written in MPIDE 0023-windows-20140316 . 


char inputString[80];       // a String to hold incoming data
boolean stringComplete = false;  // whether the string is complete
int curStrIdx = 0;


int PIN_CLR   =   8;
int PIN_CLK   =   9;

#define PIN_ANALOG  A1

#define CS_INACTIVE  1
#define CS_ACTIVE    0

// AD7940 pinout
#define AD7940_SPI_MISO    5
#define AD7940_SPI_CS      6      
#define AD7940_SPI_CLK     7


// Frames
//#define MAX_BASE_FRAMES  500
//#define MAX_BASE_FRAMES  250
#define MAX_BASE_FRAMES  100
//#define _8BIT

#ifdef _8BIT
#define MAX_FRAMES      MAX_BASE_FRAMES*2
uint8_t frames[MAX_FRAMES][64];
#else
#define MAX_FRAMES      MAX_BASE_FRAMES
uint16_t frames[MAX_FRAMES][64];
#endif


// Frame variables
// Magnetic tile reading
int pixelOrder[] = {26, 27, 18, 19, 10, 11, 2, 3, 1, 0, 9, 8, 17, 16, 25, 24};
int subtileOrder[] = {0, 2, 1, 3};
int subtileOffset[] = {0, 4, 32, 36};
uint16_t frame[64]; 

int numFrames = 0;
int curFrame = 0;

#define MODE_IDLE          0  
#define MODE_LIVE          1
#define MODE_HIGHSPEED1    2
#define MODE_HIGHSPEED2    3
#define MODE_HIGHSPEED3    4
#define MODE_HIGHSPEED4    5

int curMode = MODE_IDLE;



/*
 * Analog Read
 */
 
int readMagnetometer() {
  //return 0;
  return analogRead(PIN_ANALOG);
  //return readInternalADC();
  //return readAD7940();
  //return read_ad7940();
}

// Take one measurement form the internal ADC
int readInternalADC() {
  int numSamples = 2;
  float sum = 0.0f;
  for (int i=0; i<numSamples; i++) {
    int sensorValue = analogRead(PIN_ANALOG);
    sum += sensorValue;
  }
  sum /= numSamples;
  
  //return sensorValue;
  return int(floor(sum));
}
c
// Take one measurement from an external AD7940 14-bit ADC (SPI)
uint16_t readAD7940() {
  uint16_t value = 0;
  uint16_t delay_time = 2;
  // Idle
  digitalWrite(AD7940_SPI_CS, HIGH);   
  digitalWrite(AD7940_SPI_CLK, HIGH);  
    
  // Enable
  digitalWrite(AD7940_SPI_CS, LOW);    
  
  // Read 16 bits
  for (int i=0; i<16; i++) {
    char bit = digitalRead(AD7940_SPI_MISO);
    digitalWrite(AD7940_SPI_CLK, LOW);  
//    delayMicroseconds(delay_time);

    value = value << 1;    
    value = value + (bit & 0x01);   
    digitalWrite(AD7940_SPI_CLK, HIGH);     
//    delayMicroseconds(delay_time);    
  }
  // Disable
  digitalWrite(AD7940_SPI_CS, HIGH);    
//  delayMicroseconds(delay_time);
  
  return value;    
}



/*
 * Magnetic Sensors
 */

void clearCounter() {
  digitalWrite(PIN_CLR, 0);
  //delay(10);
  digitalWrite(PIN_CLR, 1);
  //delay(10);
}

void incrementCounter() {
  digitalWrite(PIN_CLK, 1);
  //delay(1);
  digitalWrite(PIN_CLK, 0);
  //delay(1);
}


/*
 * Capture one frame from imaging array
 */ 
void readTileFrame() {
   
  clearCounter();
  incrementCounter();
   
  for (int curSubtileIdx=0; curSubtileIdx<4; curSubtileIdx++) {
    for (int curIdx=0; curIdx<16; curIdx++) {
      // Read value
      int value = readMagnetometer();  
  
//    Serial.println(value);
//    delay(10);
 
      // Store value in correct frame location
      int frameOffset = pixelOrder[curIdx] + subtileOffset[subtileOrder[curSubtileIdx]];
      //Serial.println(frameOffset);
      //delay(25);
      frame[frameOffset] = value;   

      // Increment to next pixel
      incrementCounter();
    }
  }
  
}

// Display current frame on serial console
void displayCurrentFrame() {
  // Display frame
//  Serial.println ("\nCurrent Frame");
  int idx = 0;    
  for (int i=0; i<8; i++) {
    for (int j=0; j<8; j++) {
      Serial.print( frame[idx] );
      Serial.print( " " );        
      idx += 1;
    }
    Serial.println("");
  }    
  Serial.println("*");  
  
}


// Record MAX_FRAMES, as fast as possible
void recordHighSpeedFrames(int frameDelayTime) {
  long startTime = millis();
  
  for (int curFrame=0; curFrame<MAX_FRAMES; curFrame++) {
    // Read one frame
    readTileFrame();
          
    // Store frame
    #ifdef _8BIT
      for (int a=0; a<64; a++) {
        frames[curFrame][a] = frame[a] >> 2;
      }
    #else
      for (int a=0; a<64; a++) {
        frames[curFrame][a] = frame[a];
      }
    #endif        
    
    if (frameDelayTime > 0) {
     delay(frameDelayTime);
    } 
  } 
  
  long endTime = millis();
  Serial.print("Framerate: "); 
  Serial.println((float)MAX_FRAMES / ((float)(endTime-startTime)/1000.0f));           
    
}  


// Playback the high speed frames stored 
void playbackHighSpeedFrames() {
  
  for (int curFrame=0; curFrame<MAX_FRAMES; curFrame++) { 
    // Display frame
//    Serial.print ("\nFrame ");
//    Serial.println (curFrame);
    
    int idx = 0;    
    for (int i=0; i<8; i++) {
      for (int j=0; j<8; j++) {
        Serial.print( frames[curFrame][idx] );
        Serial.print( " " );        
        idx += 1;
      }
      Serial.println("");
    }    
        
    Serial.println("*");
    delay(50);
  }
  

  
}



long startTime = 0;
void setup() {
  // Setup pin modes
  pinMode(PIN_CLR, OUTPUT);
  pinMode(PIN_CLK, OUTPUT);

  // AD7940 ADC Pin modes
  pinMode(AD7940_SPI_CS, OUTPUT);
  pinMode(AD7940_SPI_CLK, OUTPUT);
  pinMode(AD7940_SPI_MISO, INPUT);


  // Setup initial states
  incrementCounter();
  clearCounter();
  
  // initialize serial:
  Serial.begin(115200);
  
  Serial.println ("Initializing.... Press L (live) or H (high speed), 1, 2, 3, or S (idle)");
  
  clearCounter();
  incrementCounter();  
  delay(100);

  startTime = millis();
}



void loop() {

  /*
   *  Parse serial data (if any)
   */ 
  if (Serial.available()) {
    serialEvent();
  }
   
  // print the string when a newline arrives:
  if (stringComplete) {
    Serial.println(inputString);

    if (strcmp(inputString, "L") == 0) {
      Serial.println("Live");
      curMode = MODE_LIVE;

    } else if ((strcmp(inputString, "H") == 0) || (strcmp(inputString, "1") == 0)) {
      Serial.println("High-speed Save1");
      curMode = MODE_HIGHSPEED1;

    } else if (strcmp(inputString, "2") == 0) {
      Serial.println("High-speed Save2 (1000hz)");
      curMode = MODE_HIGHSPEED2;

    } else if (strcmp(inputString, "3") == 0) {
      Serial.println("High-speed Save3 (500hz)");
      curMode = MODE_HIGHSPEED3;

    } else if (strcmp(inputString, "4") == 0) {
      Serial.println("High-speed Save4 (250hz)");
      curMode = MODE_HIGHSPEED4;

    } else if (strcmp(inputString, "S") == 0) {
      Serial.println("Idle");
      curMode = MODE_IDLE;
    }
    
    Serial.print("Input: ");
    Serial.println(inputString);
    // clear the string:
    strcpy(inputString, "");
    curStrIdx = 0;
    stringComplete = false;
  }

  
  /*
   * Take action based on current mode
   */
  if (curMode == MODE_LIVE) {
    readTileFrame();
    displayCurrentFrame();
    
  } else if (curMode == MODE_HIGHSPEED1) {
    // Full/maximum speed
    recordHighSpeedFrames(0);
    playbackHighSpeedFrames();
    curMode = MODE_IDLE;
    
    Serial.println ("Initializing.... Press L (live) or H (high speed), 1, 2, 3, or S (idle)");

  } else if (curMode == MODE_HIGHSPEED2) {
    // ~1000Hz
    recordHighSpeedFrames(1);
    playbackHighSpeedFrames();
    curMode = MODE_IDLE;
    
    Serial.println ("Initializing.... Press L (live) or H (high speed), 1, 2, 3, or S (idle)");

  } else if (curMode == MODE_HIGHSPEED3) {
    // ~500Hz
    recordHighSpeedFrames(2);
    playbackHighSpeedFrames();
    curMode = MODE_IDLE;
    
    Serial.println ("Initializing.... Press L (live) or H (high speed), 1, 2, 3, or S (idle)");
    
  } else if (curMode == MODE_HIGHSPEED4) {
    // ~250Hz    
    recordHighSpeedFrames(4);
    playbackHighSpeedFrames();
    curMode = MODE_IDLE;
    
    Serial.println ("Initializing.... Press L (live) or H (high speed), 1, 2, 3, or S (idle)");
    
  }


  
  //delay(10);
  
  
}



/*
  SerialEvent occurs whenever a new data comes in the hardware serial RX. This
  routine is run between each time loop() runs, so using delay inside loop can
  delay response. Multiple bytes of data may be available.
*/
void serialEvent() {
  while (Serial.available()) {
    // get the new byte:
    char inChar = (char)Serial.read();
    // if the incoming character is a newline, set a flag so the main loop can
    // do something about it:
    if (inChar == '\n') {
      stringComplete = true;
    } else {
      // add it to the inputString:
      inputString[curStrIdx] = inChar;
      curStrIdx += 1;
      
    }
  }
}

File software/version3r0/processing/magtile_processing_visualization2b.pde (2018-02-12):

// Magnetic Imager Tile v3 Processing Visualization
// This code is intended to pair with the Arduino/Chipkit code for reading data 
// from the magnetic imager tile v3, and streaming it through a Serial port. 
//
// Two 8x8 grids are shown: a normal gain (top) and high-gain (bottom).  The 
// high-gain is particularly useful for low-intensity fields. 
//
// Keys (lower-case): 
//   L  - Live mode.  Press this to start streaming data live from the tile. 
//  1-4 - High-speed capture.  Capture a number of high-speed frames (set in 
//        the Chipkit code) from the tile, and stream them back.  Note that 
//        the actual framerate will depend upon the code/platform/ADC.  The 
//        values displayed here (1 ~= ~2000Hz, 4 ~= 250Hz) are calibrated
//        from my Chipkit MAX32 platform, and may vary quite a bit if you're
//        using a different platform or code. 
//   C  - When in LIVE mode, it's possible to press 'C' and calibrate out 
//        the background level for each tile, to reduce the noise.  If you 
//        do this, ensure that no fields are present on the tile.  
//        Alternatively: If a static field is present on the tile, this 
//        will help show changes to that static field. 
//
// Serial port: The serial port index is hard-coded in, and you will likel
//  have to change this for your platform.  See the //## comment marker in 
//  the setup() function.
//


import processing.serial.*;

// Serial port vairables. 
Serial myPort;  // Create object from Serial class
int val;        // Temporary variable storing data received from the serial port

// Array of x/y coordinates recieved over serial port.  Maximum number of recordings to store is MAX_RECORDINGS. 
int MAX_SIZE = 8;
int[][] data = new int[MAX_SIZE][MAX_SIZE];
int curDataIdx = 0;      // Index of array element that has highest populated value (-1)

// Font (for drawing text)
PFont fontA;

// Screenshot index (for taking screenshots). 
int screenshot_number = 0;

int numCalibFrames = 0;
int maxCalibFrames = 200;
int calibrationEnabled = 0;
int[][] dataCalib = new int[MAX_SIZE][MAX_SIZE];
int isCalibrated = 0;

String curText = "text";


// Called whenever there is serial data available to read
void serialEvent(Serial port) {
  // Data from the Serial port is read in serialEvent() using the readStringUntil() function with * as the end character.
  String input = port.readStringUntil(char(10)); 
  
  if (input != null) {
    // Helpful debug message: Uncomment to print message received   
    println( "Receiving:" + input);
    input = input.trim();    
    int split_point = input.indexOf(' ');
    if (split_point <= 0) {
      curDataIdx = 0;
      return;        // If data does not contain a comma, then disregard it.
    } else {
      // Parse data
      // The data is split into an array of Strings with a comma or asterisk as a delimiter and converted into an array of integers.
      float[] vals = float(splitTokens(input, " "));      
      if (vals.length != MAX_SIZE) return;
      
      // Store data      
      for (int i=0; i<MAX_SIZE; i++) {
        data[curDataIdx][i] = int(vals[i]);
        
        if (calibrationEnabled == 1) {
          dataCalib[curDataIdx][i] += int(vals[i]);                    
        }
      }
      
      // Increment index that we store new data at.      
      curDataIdx += 1;
      if (curDataIdx >= MAX_SIZE) {
        curDataIdx = 0;
        
        if (calibrationEnabled == 1) {
          numCalibFrames += 1;
          
          if (numCalibFrames > maxCalibFrames) {
            calibrationEnabled = 0;
            calibration();
          }
        }
      }
      
      // Helpful debug message: Display serial data after parsing. 
      //println ("Parsed x:" + x + "  y:" + y);
    }
  }
  
  /*
      // Mask
    for (int i=0; i<12; i++) {
      for (int j=0; j<12; j++) {
        if ((i >= 2) && (i<= 7) && (j >= 2) && (j <= 9)) {
          if (j == 9) {
            data[i][j] = 400 - data[i][j];
          }
          // keep existing data
        } else {
          data[i][j] = 200;
        }
      }
    }
  */
  
}


void calibration() {
  
  println("Calibration Data:");
  for (int i=0; i<MAX_SIZE; i++) {
    for (int j=0; j<MAX_SIZE; j++) {
      dataCalib[i][j] = floor((float)dataCalib[i][j] / (float)maxCalibFrames);
      print (dataCalib[i][j] + "  ");      
    }
    println("");
  }
  
  isCalibrated = 1;
  curText = "";
  
  
}
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

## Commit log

2017-07-29 added v2r0 hardware
    [magarray-halleffect.kicad_pcb, magarray-halleffect.sch]
2017-07-29 Added python example for raspberry pi
2017-07-29 Added Arduino and Processing code
2017-12-31 Added v3r0 imager tile, a smaller 8x8 version of v2, with a binary counter incrementing interface
    [magarray-halleffect-v3r0.brd, magarray-halleffect-v3r0.sch]
2019-09-13 Added Python/Raspberry Pi example for magnetic tile version 3

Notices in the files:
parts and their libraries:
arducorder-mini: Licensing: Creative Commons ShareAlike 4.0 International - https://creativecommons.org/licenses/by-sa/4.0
